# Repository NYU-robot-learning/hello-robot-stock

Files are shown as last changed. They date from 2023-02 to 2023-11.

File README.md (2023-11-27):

# Stick Stocks

**Special thanks to Anya Zorin and Jyo Pari for their help in designing and testing these stocks.**

## Full Picture
### Stick
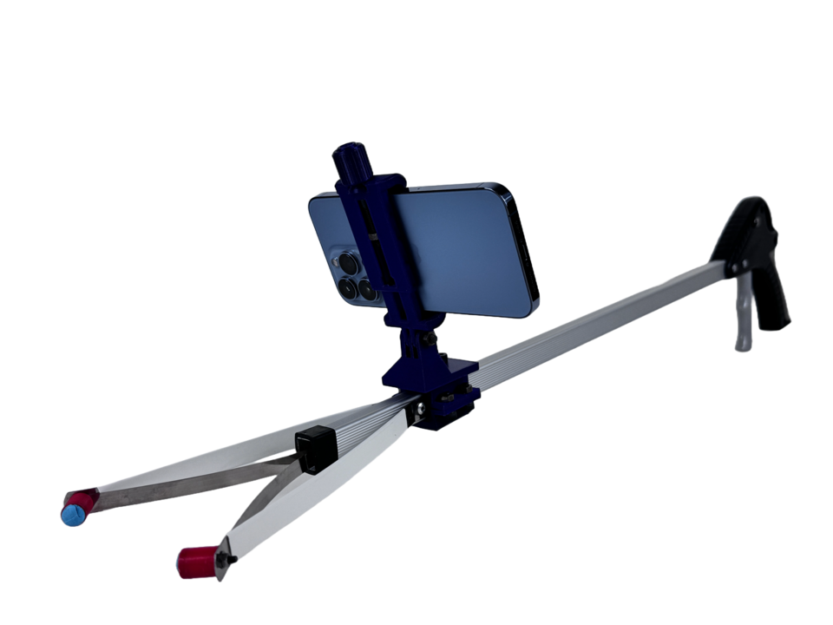
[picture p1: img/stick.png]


### Robot gripper
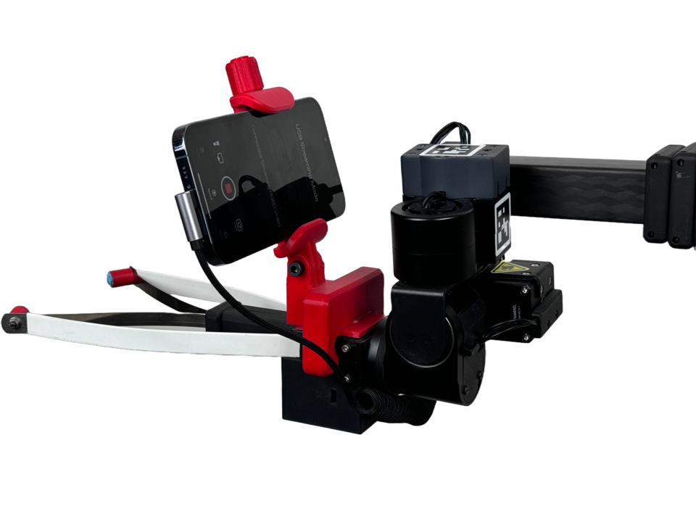
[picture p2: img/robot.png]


These stocks were designed for collecting data and running expirements at the [NYU Generalized Robotics and AI Lab](https://lerrelpinto.com) using the [Hello Robot Stretch](https://hello-robot.com/product) with an iPhone as an egocentric camera. For data collection the iPhone was mounter to a manual [grabber tool](https://www.amazon.com/Vive-Suction-Reacher-Grabber-Pack/dp/B07GFL168C/ref=sr_1_7?keywords=grabber+tool+suction+cups&sr=8-7), and calibrated to be at the same perspective as the iPhone on the robot. Over time the design has been adjusted to fit the specific setup by adjusting height and setback of the clamps so that the two views are properly aligned, with the tips of the gradder arm as points of reference.

## [Bill of Materials](https://docs.google.com/spreadsheets/d/1qkDV2W64Q2eQ5Y6DkTYfokI8hO4we7ong_2VNufDRaY/edit?usp=sharing) 
All necessary materials and hardware for this setup is listed in the Bill of Materials.

## 3D Printing and Files
Each different stock has its own folder, within each part has its folder conatining the following parts for each file: .STEP, .STL, .gcode, and a .f3d file. 
For the stocks, most parts are 3D printed on the [Original Prusa i3 MK3S+](https://www.prusa3d.com/category/original-prusa-i3-mk3s/), so the gcode is for that specific printer. 

## Phone Holder
### The phone holder is taken from the [Modular Mounting System by HeyVye](https://www.thingiverse.com/thing:2194278), which is licensed under the [Creative Commons - Attribution](https://creativecommons.org/licenses/by/4.0/) license.

It uses the Mount Phone Clamp, and the print files, print instructions, and instructions for assembly are all on the linked page. The files are also provided in the folder [PhoneHolder](PhoneHolder/)

For the hardware, instead of a printed bolt and nut, a M5 35mm bolt and a M5 nut for better durability and performance. 

The attachment joint/mechanism is taken from this system, but it is important to note that within the system the joint is inspired from a gopro mount joint, so it will work with a standard gopro mount as well. There is more on this in the [Attachment Joint/Mechanism](#attachment-jointmechanism) section. 

<!-- [PhoneClamp_body1.stl](PhoneHolder/PhoneClamp_body1.stl)

[PhoneClamp_body2.stl](PhoneHolder/PhoneClamp_body2.stl)

[PhoneClamp_Knob.stl](PhoneHolder/PhoneClamp_Knob.stl) -->
## Robot Clamp
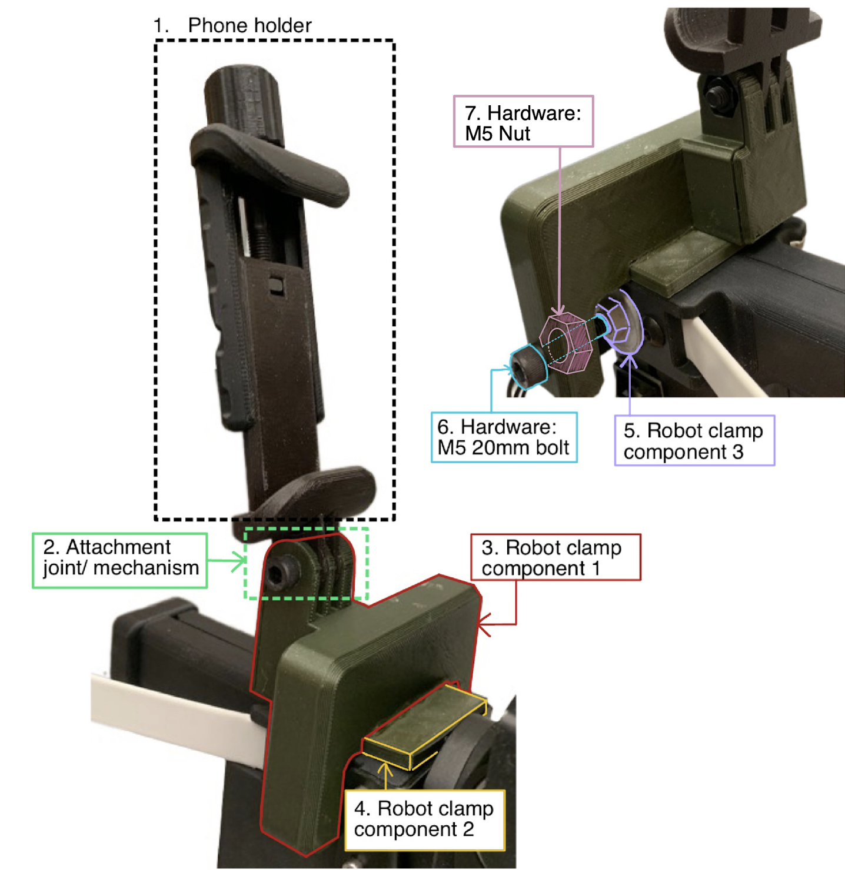
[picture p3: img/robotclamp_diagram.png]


### Part Files
1. [Phone Holder](#phone-holder)
2. [Attachment joint/mechanism](#attachment-jointmechanism)
3. Clamp Component 1: [robotClamp.stl](RobotClamp/robotClamp)
4. Clamp Component 2: [robotClamp_insert.stl](RobotClamp/robotClamp_insert/)
5. Clamp Component 3: [robotClamp_pad.stl](RobotClamp/robotClamp_pad.stl)

### Hardware and other items for assembly
6. 1 x M5 20mm bolt, socket head
7. 1 x M5 nut
- [Gorilla Super Gel Glue](https://www.amazon.com/Gorilla-7700108-2-Pack-Super-Clear/dp/B00OAAUAX8?source=ps-sl-shoppingads-lpcontext&ref_=fplfs&smid=ATVPDKIKX0DER&th=1)

### Assembly Instructions
1. Print necessary files. Each respective file folder contains suggested print, support, and orientation settings. 
2. Assemble phone holder using instructions in the [Phone Holder](#phone-holder) section. 
3. Take the robot clamp components 1 and 2 ([robotClamp.stl](RobotClamp/robotClamp.stl) and [robotClamp_insert.stl](RobotClamp/robotClamp_insert.stl)), add super glue to the underpart of component 1 in which component 2 can be inserted into. 
4. Press component 2 into component 1 where the glue has been applied, such that component 2 is centered and equal amounts stick out from the clamp. Hold down for at least 15 sec. (Note that the glue takes around a day to fully set)
5. Insert nut into slot as shown in image

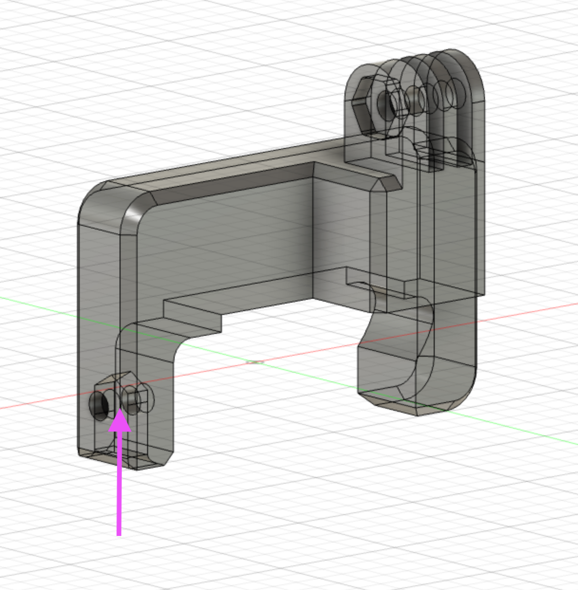
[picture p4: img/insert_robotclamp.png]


6. Insert screw/bolt into hole, thread through the nut that was inserted into clamp at step 5 using a 4mm allen key, and once the end is visible, thread the silver end pad([Robot clamp component 3](RobotClamp/robotClamp_pad.stl)) onto the end of the screw. 

7. Follow the instructions in the [attachment mechanism](#attachment-jointmechanism) section to attach the phone holder. 

## Grabber Clamp
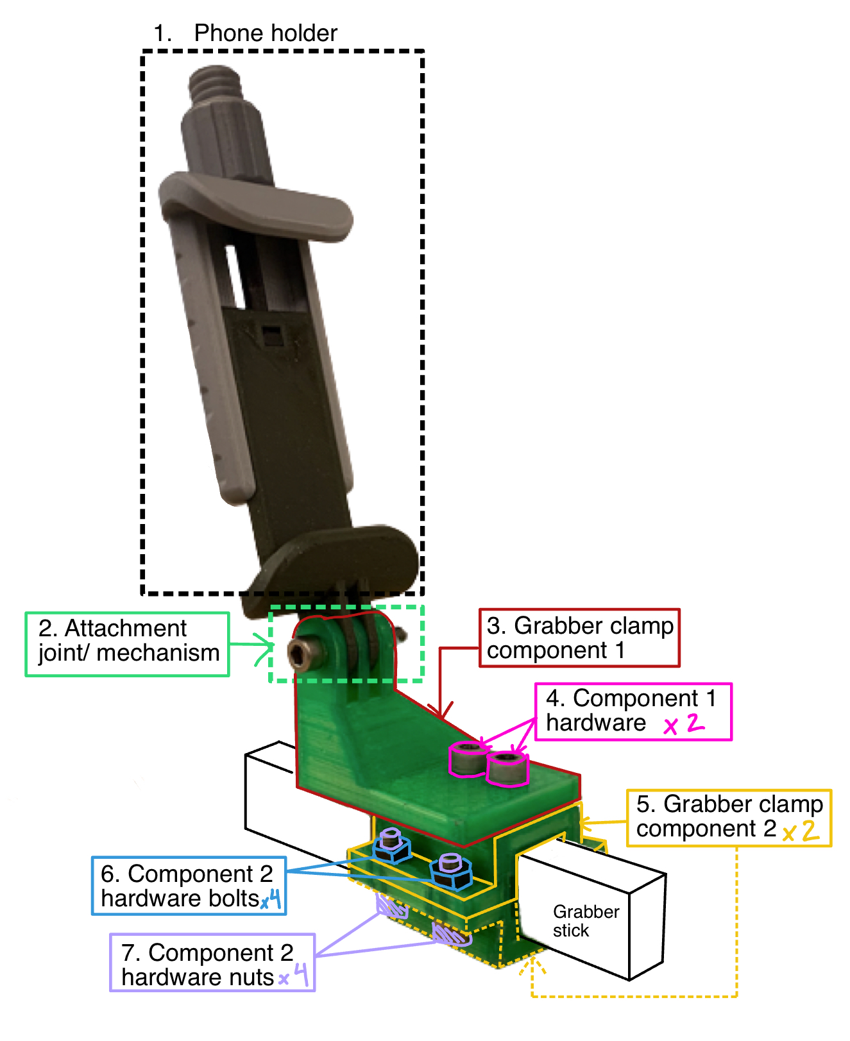
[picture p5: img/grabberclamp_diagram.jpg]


### Part Files
1. [Phone Holder](#phone-holder)
2. [Attachment joint/mechanism](#attachment-jointmechanism)
3. [Grabber Clamp Component 1](GrabberClamp/grabberClamp_top.stl)
5. [Grabber Clamp Component Top and Bottom](GrabberClamp/grabberClamp_body/)

### Hardware
4. 2 x M5 10mm bolts
6. 4 x M5 nuts
7. 4 x M5 12mm bolts

### Assembly Instructions
1. Print necessary files. Each respective file folder contains suggested print, support, and orientation settings. 
2. Take the two clamp body component 2, and press them together around the clamp as shown in the diagram, making sure the holes align. The holes oriented such that they are closer to the tips than where you hold the stick.
3. Take the #7 (the 4 M5 12mm bolts) and the 4 M5 nuts and use them to attach the two peices together with a 4mm allen key, but do not tighten all the way down, first get all the bolts secure with the nuts. 
4. Once all the bolts and nuts are in place, tighten one down until you feel resistence, then do the same with the diagonal one, and repeat for the remaining two. Continue this criss cross pattern of tightening till the clamp is secure. Using this method ensures that the clamp is not tightened at an angle and the bolts are tightened evenly. This is important, because if the clamp is attached at an angle, the camera view may also be tilted.
5. Place the grabber component 1 ([grabberClamp_top.stl](GrabberClamp/grabberClamp_top.stl)) on top of the clamp and line up the holes on the part and the clamp. The back of component 1 should align with the back of the clamp. There should be none of the top of the component 2 visible. 

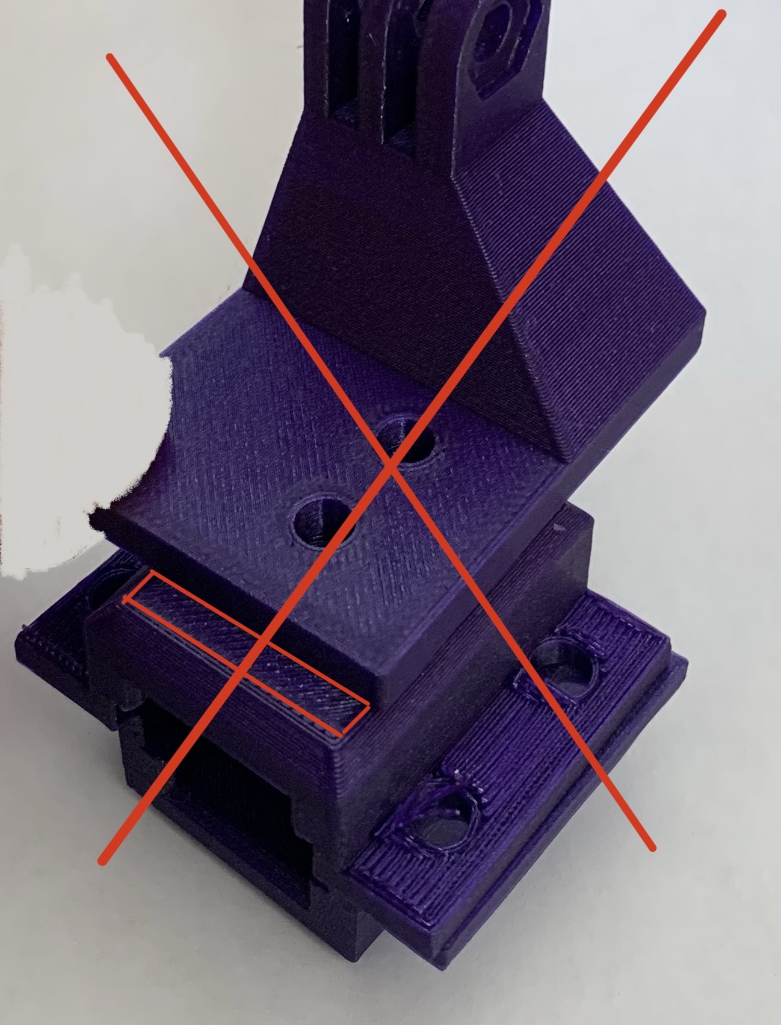
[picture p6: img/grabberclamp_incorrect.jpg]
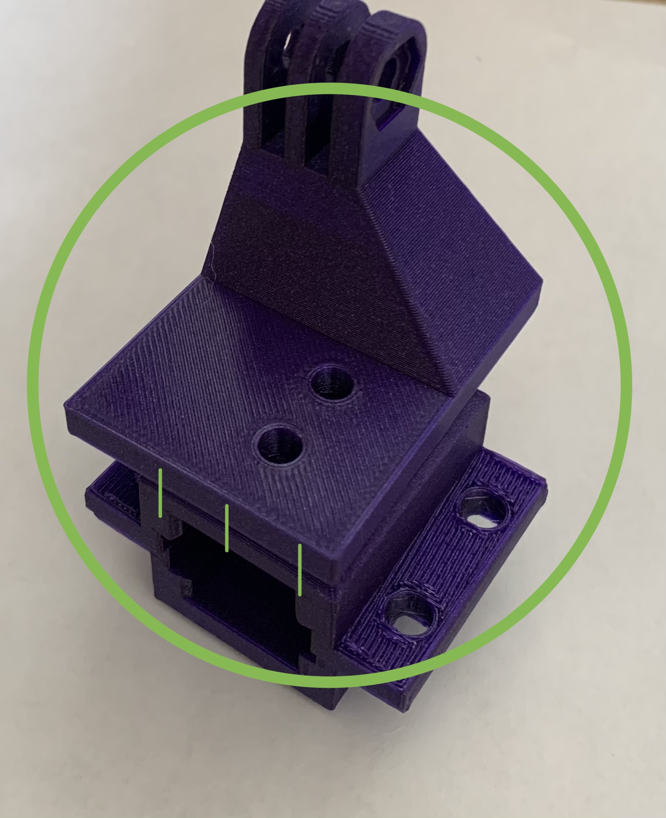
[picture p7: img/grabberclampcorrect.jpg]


6. Take the two M5 10mm bolts and screw them into the top piece with a 4mm allen key, and then into the clamp. The bolts will thread into the plastic and be secure. Do not remove these bolts and rescrew them because this will strip the threads created by the first time you secured the part. 
7.  Follow the instructions in the [attachment mechanism](#attachment-jointmechanism) section to attach the phone holder. 
## Grabber Ends
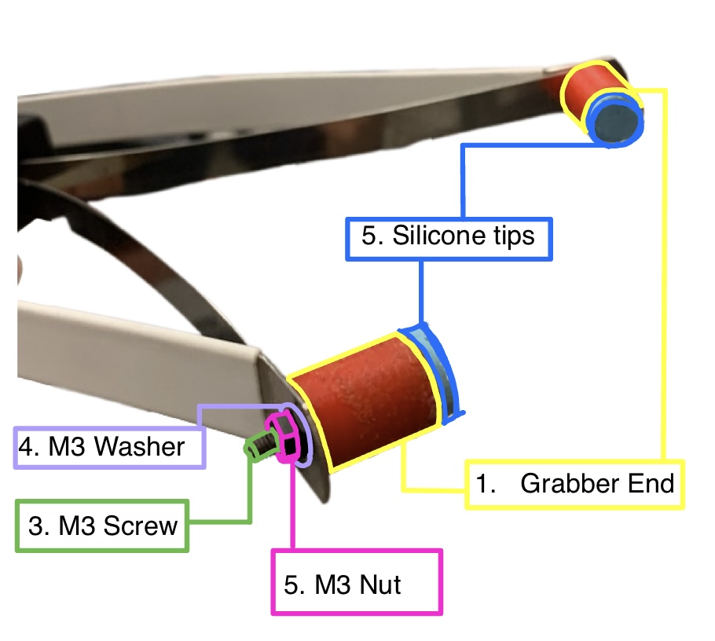
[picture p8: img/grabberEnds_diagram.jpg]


### Part Files
1. [Grabber End](GrabberEnds/grabberEnd.stl)
2. [Grabber End Mold](GrabberEnds/grabberEnd_mold.stl)

### Hardware
3. M3 8mm socket head bolt
4. M3 Washer
5. M3 Nut

### Other Materials
5. Two part silicone ([Oomoo 25](https://www.amazon.com/Smooth-OOMOO-25-Curing-Silicone/dp/B01C4YQ4TU/ref=sr_1_3?keywords=oomoo+25&sr=8-3))
- Tape (of any kind)
- [Gorilla Super Gel Glue](https://www.amazon.com/Gorilla-7700108-2-Pack-Super-Clear/dp/B00OAAUAX8?source=ps-sl-shoppingads-lpcontext&ref_=fplfs&smid=ATVPDKIKX0DER&th=1)

### Molding Process for Silicone Tips
1. Pre mix the silicone as instructed on the box
2. Take the two halves of the molds and tape them together as in the image. Make sure that the bottom is flat by placing on a flat surface while taping. 
3. Pour the silicone in to the mold. 
4. Let it cure for the amount of time specified on the box, and then untape the two peices and gently remove the silicone tip. 

### Assembly Video

### Assembly instructions
1. Take the printed red tip ([Grabber End](GrabberEnds/grabberEnd.stl)) and insert the M3 8mm bolt into the tip as shown in the video. You may have to push it all the way down with a 2mm allen key. 
2. Take the glue and line the inside of the tip with it.
3. Press the silisone tip into the red end and press it down for at least 30 seconds. It is important to use the listed glue as it bonds to both silicone and plastic. 
4. Remove the stock ends of the grabber hand, and attach the new end by first inserting the bolt through the hole, then putting the M3 Washer, and then screwing the M3 Bolt onto the bolt.
5. To secure the bolt, use a small adjustable wrench, or sometimes simply using your hand will tighten the end enough. 
6. Repeat this process for the other side. 

## Attachment Joint/Mechanism
[INESRT IMG OF FULL THING]
The attachment mechanism used is a ispired from the GoPro Mounting system, so this system wil also work with any standard GoPro mounts. 

### Hardware
1. M5 20mm socket head
2. M5 Nut

### Instructions
1. Take the two peices you are trying to attach together (i.e. phone holder and robot clamp) and locate the attachment point as in the picture:

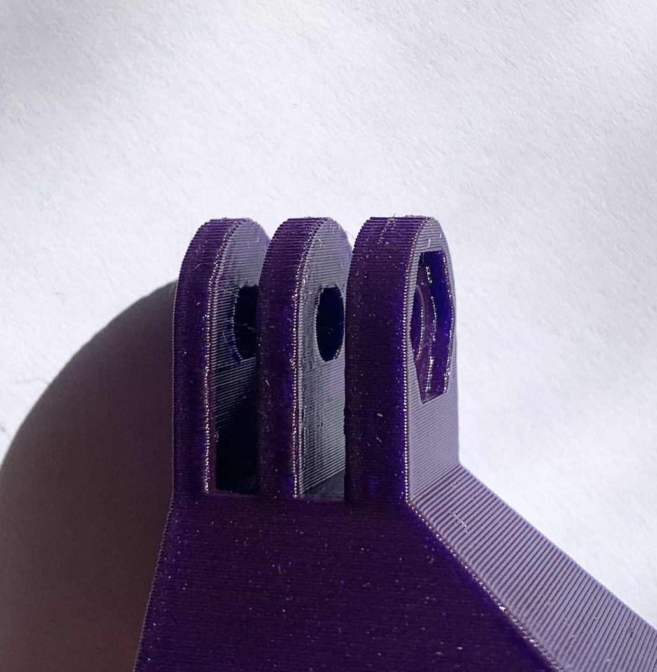
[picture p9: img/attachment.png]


2. These two peices slot together, and the center holes should align. Make sure that the peices are oriented correctly by referring to the [Full Assembly](#full-picture). 
3. Insert the M5 bolt from the side that does *not* have a hexagonal indentation. 
4. Once the bolt is all the way through, screw the M5 nut on from the other side, and tighten using a 4mm allen key, and a small wrench if needed. 

## Tilt Calibration
When calibrating the tilt of the iPhones, since the attachment joint is adjustable, the app [INSERT NAME] was used. Put the stick on a surface level to the ground like in the image below and calibrate. Find a block that the robot clamp can fit on (a lot of charging blocks work) and place it on a level surface, then calibrate using the app. Then place back on robot.

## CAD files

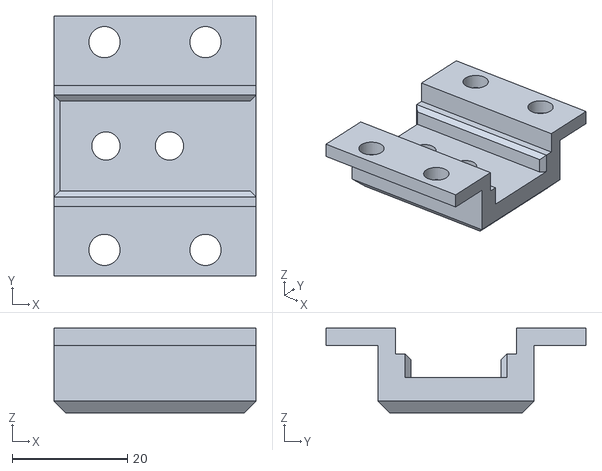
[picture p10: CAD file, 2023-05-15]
grabberClamp/grabberClamp_body/grabberClamp_body.stl
35.0 x 45.0 x 14.6

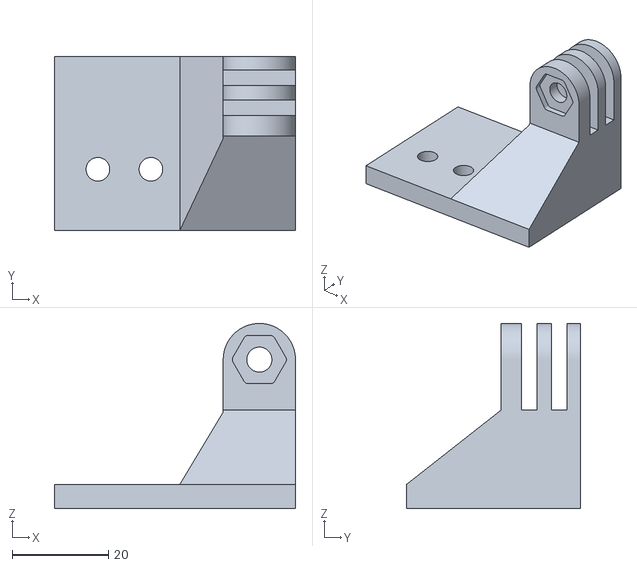
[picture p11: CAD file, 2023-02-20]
grabberClamp/grabberClamp_top/grabberClamp_top.stl
50.0 x 36.1 x 38.4

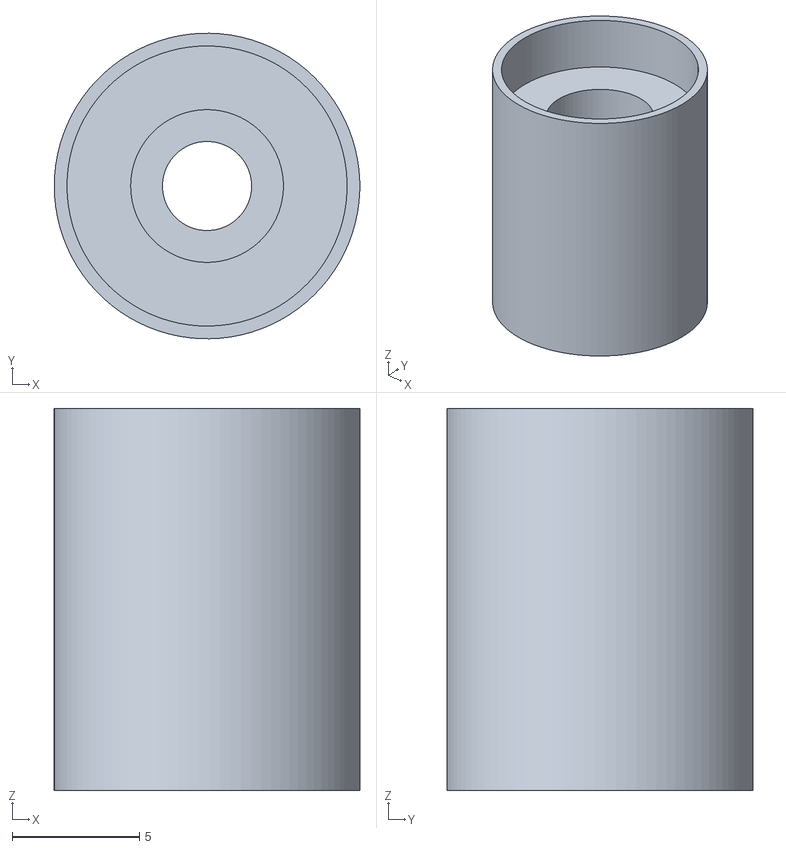
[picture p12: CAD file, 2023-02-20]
grabberEnds/grabberEnd/grabberEnd.stl
12.0 x 12.0 x 15.0

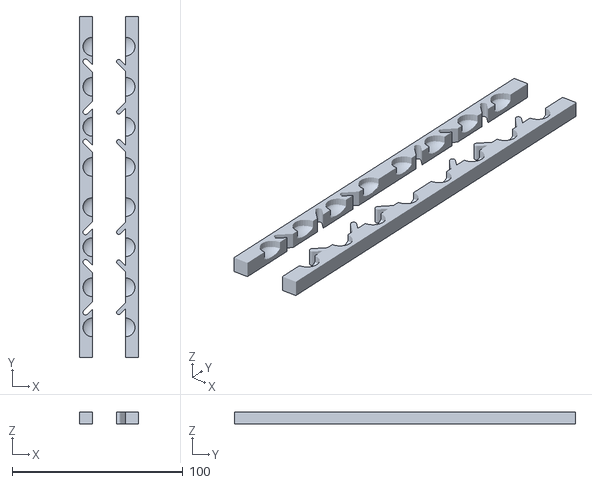
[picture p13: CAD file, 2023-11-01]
grabberEnds/grabberEnd_longMold/grabberEnd_longMold.stl
34.5 x 200.0 x 7.00

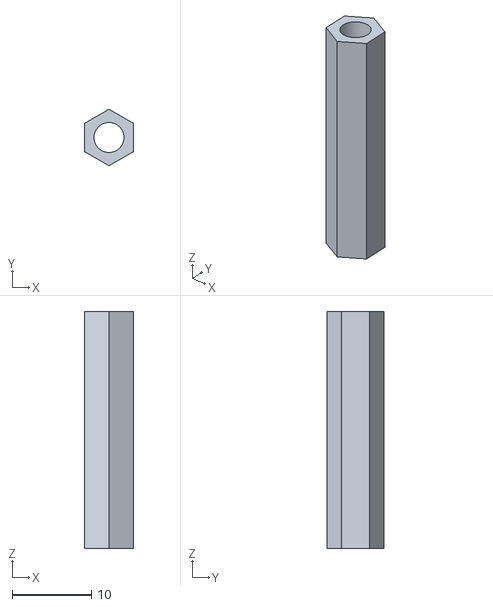
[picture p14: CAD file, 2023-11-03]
phoneHolder/knobTightner/knobTightner.stl
6.20 x 7.16 x 30.0

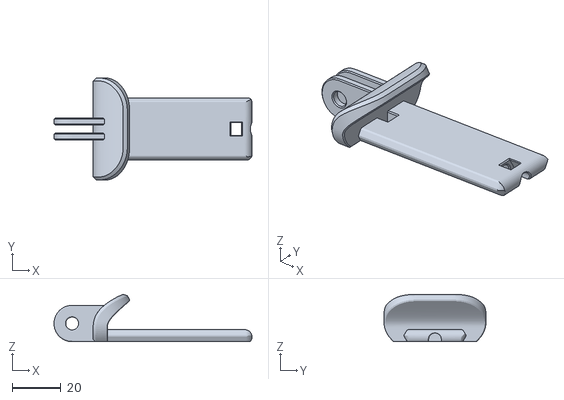
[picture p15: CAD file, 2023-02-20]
phoneHolder/phoneClamp_bottom/phoneClamp_bottom.stl
81.5 x 42.0 x 19.6

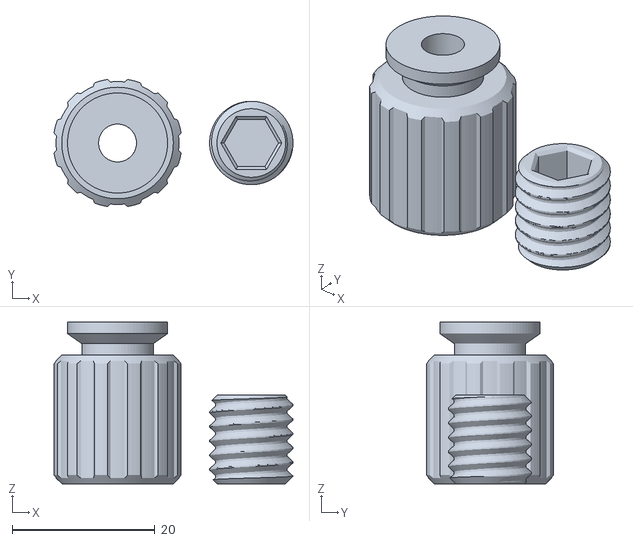
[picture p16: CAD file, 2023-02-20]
phoneHolder/phoneClamp_knob/phoneClamp_knob.stl
33.4 x 17.8 x 22.6

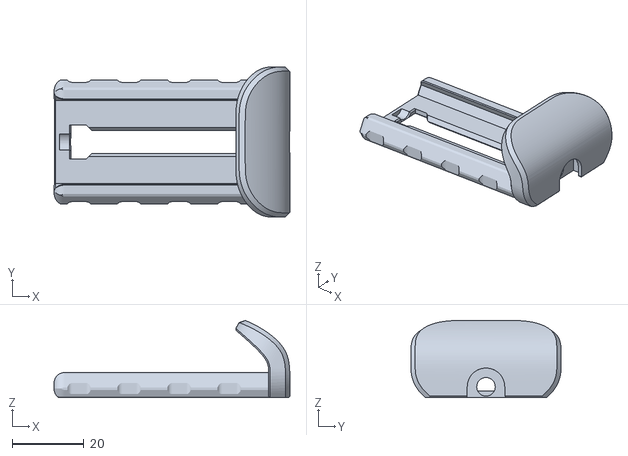
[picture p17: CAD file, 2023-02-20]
phoneHolder/phoneClamp_top/phoneClamp_top.stl
66.0 x 42.0 x 21.6

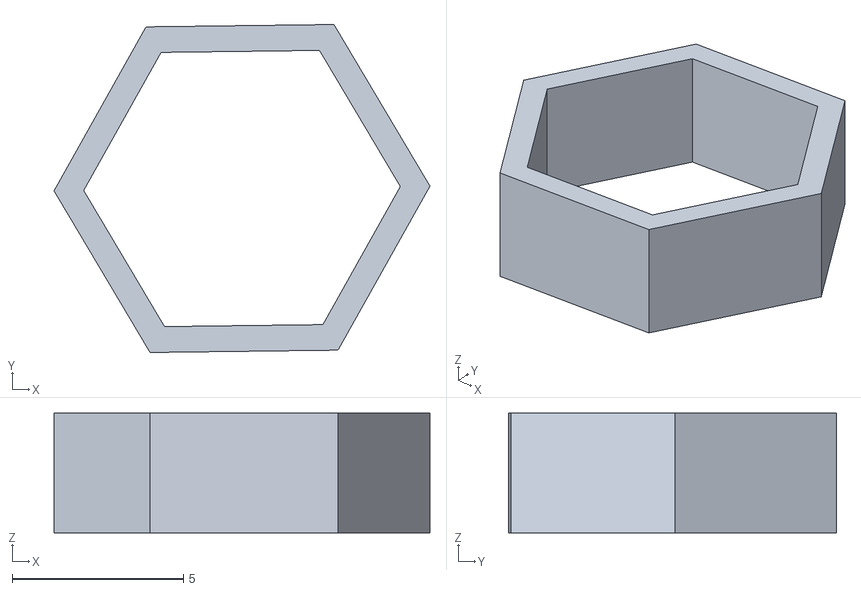
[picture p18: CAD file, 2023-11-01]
robotClamp/hexnutBorder/hexnut-border.stl
11.0 x 9.57 x 3.50

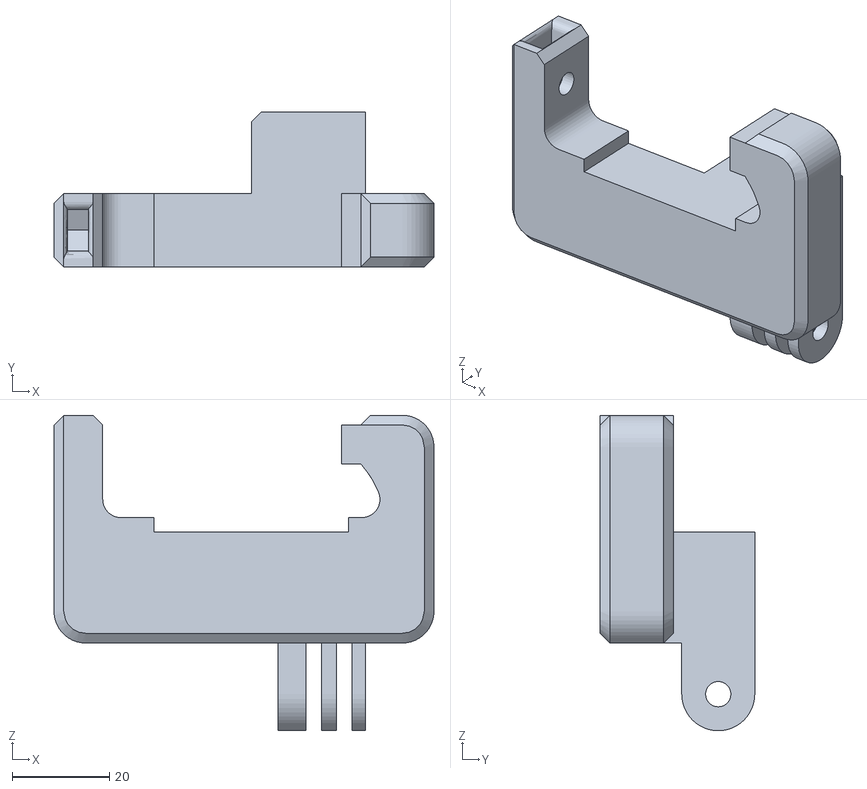
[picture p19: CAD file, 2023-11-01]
robotClamp/robotClamp/robotClamp.stl
78.0 x 31.7 x 64.8

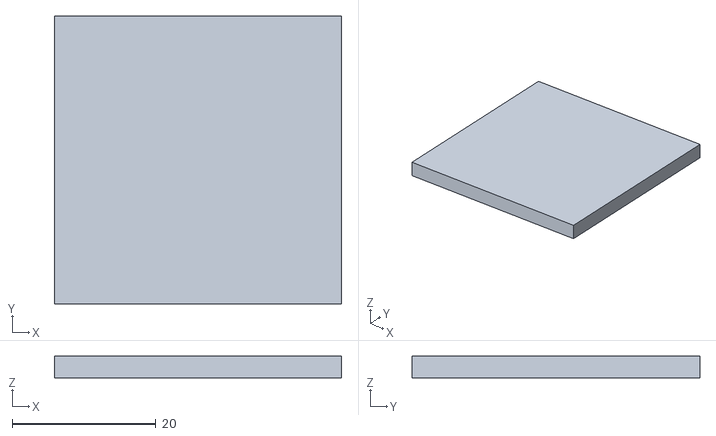
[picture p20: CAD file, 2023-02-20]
robotClamp/robotClamp_insert/robotClamp_insert.stl
39.9 x 40.0 x 3.00

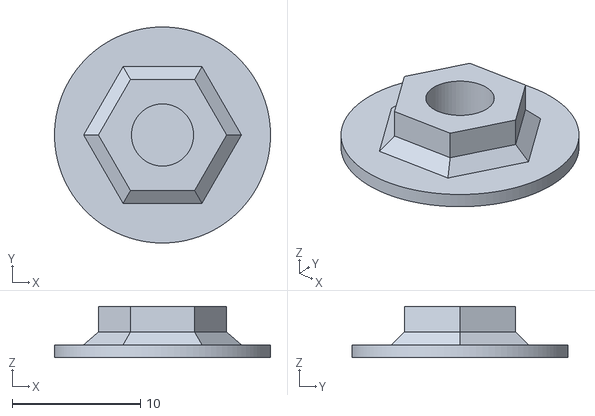
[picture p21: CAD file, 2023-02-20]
robotClamp/robotClamp_pad/robotClamp_pad.stl
16.8 x 16.8 x 4.00

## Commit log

2023-11-01 rearranged folders and updated some files
    [GrabberEnd_longMold2.stl, PhoneClamp_Knob.stl, PhoneClamp_body1.stl, PhoneClamp_body2.stl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]
2023-11-01 .gcode for bottom part of phone clamp
2023-11-03 knob tightening piece added
    [knobTightner.stl]
2023-11-05 renamed folder
    [hexnut-border.stl, robotClamp.stl, robotClamp_insert.stl, robotClamp_pad.stl]
